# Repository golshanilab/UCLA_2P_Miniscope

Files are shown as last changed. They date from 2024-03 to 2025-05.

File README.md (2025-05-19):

# UCLA 2P Miniscope 
UCLA miniature multiphoton microscope resources and design files.

The UCLA miniscope project is an open-source inititive to design open-source miniature microscopes for neuroscience. Here, we present a multiphoton miniature microscope developed at UCLA which is able to record from fine structures like dendrites, or several hundred microns into tissue.<br>
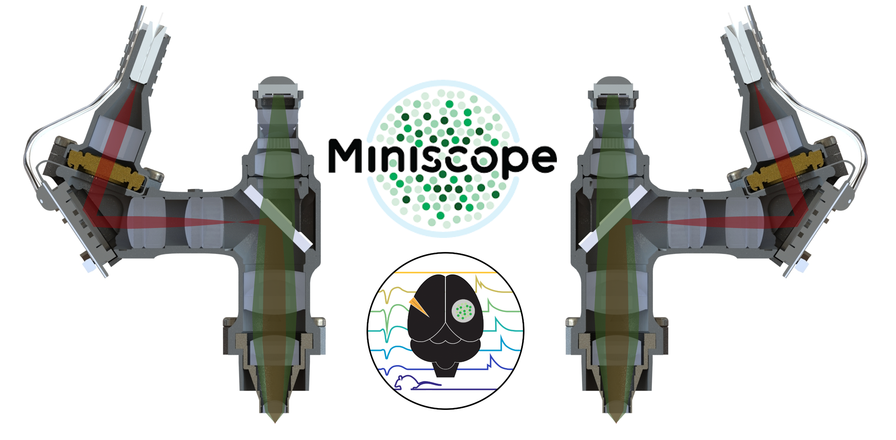
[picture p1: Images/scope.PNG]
Scope
 <br>

In this Git repository, we openly share all of the design files for this microscope with the community, these include: <br>
  - Mechanical Design Files (in .STEP format)
  - Optical Design Files (ZEMAX .ZARs)
  - Electronic PCB Designs (GERBER)
  - Control Software (Matlab and Waveforms)

<br>
As well as additional information to support users in setting up these devices, such as:

  - Suite2P analysis .ops to aid in analysis
  - A pre-trained DeepLabCut Network
  - ScanImage Machine Data Files and Configuration files
<br>

For additional information, please take a look at our bioRxiv paper [here](https://www.biorxiv.org/content/10.1101/2024.03.29.586663v1)
<br>
We also provide the following resources regarding data avialability and processing:
For a folder full of Demo resources, please visit the [Demo](https://ucla.box.com/s/3wto9k1oq8evrciismuwrfbsespp461s) UCLA Box Repository.
  - System Requirements: <br>
To analyze the data we generate, four softwares are used, [FIJI/Imagej](https://imagej.net/software/fiji/) (v.1.54f), [Suite2P](https://github.com/MouseLand/suite2p) (v.0.9.2), [DeepLabCut](https://github.com/DeepLabCut/DeepLabCut) (v.2.3.8), [MATLAB](https://www.mathworks.com/products/matlab.html) (v.2022b). Any relatively modern windows or apple computer should be capable of running all of these softwares without technical limitations, although a CUDA-compatible GPU is very useful for DeepLabCut. For this work, we tested the analysis pipeline with x64 Windows 10 Pro, v.22H2. The analysis can be completed using standard hardware, we used a Windows Book 2 from 2018 with an Intel Core i7-8650U CPU and 16BG of RAM. 

  - Software Installation Guide: <br>
Processing the data relies on well-documented software packages as well as two custom softwares. The first is a FIJI/ImageJ macro titled "Preprocess.imj" which can be installed from FIJI/ImageJ by selecting from the main toolbar "Plugins" > "Macros" > "Install" and navigating to the "Preprocess.imj" file. If you are a heavy user that anticipates routinely analyzing data, the contents of "Preprocess.imj" can be copied from the Edit Macros menu and added to the end of the "Startup Macros" file so it is installed when FIJI/ImageJ is initialized. To do so, select "Plugins" > "Macros" > "Edit" and navigate to Fiji.app\macros\StartupMacros.fiji.ijm and add the contents of "Preprocess.imj" to the end of the file. Save the file and restart Fiji/Imagej. This way the macro is installed and able to be run from the "Plugins" > "Macros" menu without installing each time.

Please reference the Suite2P, DeepLabCut, and MATLAB installation guides for assistance getting these softwares operational. The MATLAB file "SpatialFiring.m" can be run from any suitable MATLAB directory so long as "Fall.mat" and "Behavior_ExampleDLC_resnet50_2P_Miniscope_2Dec5shuffle1_100000_filtered.csv" are also present in that same directory, should you want to understand the method used in order to check the spatial firing properties of neurons within the UCLA 2P Miniscope FOV.

The total install time for the custom code is only a few minutes, installing the other standalone software can be installed within a few hours. 
    
  - Demo: <br>
Once the data is collected, there are several steps to complete the analysis. We will explain the general implementation of these steps through an example which involves processing the calcium imaging data, behavioral data, and integrating the results with a MATLAB script. 
1. First, we will condiser the calcium data. Load the .tif file "Example_Data.tif" located in the [Demo](https://ucla.box.com/s/3wto9k1oq8evrciismuwrfbsespp461s) box link, that was generated by ScanImage, into FIJI/ImageJ and preprocess using the provided "Preprocess.imj" macro. Users can also deinterleave image channels at this time. In the case of the demo, please select deinterleave on "Example_Data.tif" since it contains information from both SiPM channels. Once processed, save dynamic iamge stack (should be called "Example_Data-1.tif #1") as a .tiff ("File" > "Save As" > "Tiff"). Next initilize Suite2P v.0.9.2 and navigate to "File" > "Run Suite2P". Next, load the predefined ops.npy file in the "Load ops file" window and define the data_path field to where you saved the .tif file. Small modifications to parameters might be needed for your specific use case, these are general and what worked well in our hands. Next click "RUN SUITE2P" and wait until all data is processed. Within the "save_path" directory, there will be a "Fall.mat" file contained in the "suite2p" > "plane0" folder which we will then process. Screenshots of the expected output are included within the Demo folder as "Demo_S2P_Output.PNG". 
2. Next, analyze the time-synchronized example behavior video "Behavior_Demo.avi" with DeepLabCut. For this example, the calcium and behavior videos are not aligned. If this is your first time, please review the excellent documentation found [here](https://deeplabcut.github.io/DeepLabCut/docs/installation.html) to label data and build a trained model. We have included a pre-trained network that we used for image classification of the location of the miniscope headpiece, but it may be necessary to build your own model depending on your specific experimental conditions. Output files "Behavior_ExampleDLC_resnet50_2P_Miniscope_2Dec5shuffle1_100000_filtered.csv" are provided along with an annotated video describing the DeepLabCut outputs. Once complete, navigate to the "video" directory of your DLC model and select the DLC output .csv file and place in the same directory as the "SpatialFiring.m" file. We provide this processed .csv file as "Behavior_ExampleDLC_resnet50_2P_Miniscope_2Dec5shuffle1_100000_filtered.csv" within the "Demo" > "Expected Outputs" > "DeepLabCut" folder. 
3. Now that the calcium imaging and behavior data are analyzed, we can put the two together and assess the firing properties of individual neurons as a function of location in the behavioral chamber and time. For this purpose use the "SpatialFiring.m" file included in this repository and to the same directory add the "Fall.mat" and the output of the DLC process, which in the uploaded example is called "Behavior_ExampleDLC_resnet50_2P_Miniscope_2Dec5shuffle1_100000_filtered.csv." This will compute the spatial firing properties of the neural traces from "Fall.m" based on the spatial coordinates found in the "Behavior_ExampleDLC_resnet50_2P_Miniscope_2Dec5shuffle1_100000_filtered.csv" file.

We also provide in the [Demo](https://ucla.box.com/s/3wto9k1oq8evrciismuwrfbsespp461s) folder, the expected output from the analysis described above. The preprocessing step in FIJI/Imagej took approximately 2 minutes to complete, Suite2P analysis took 7 minutes with all of the registration steps and ROI extraction for the 1000 frames of the first channel from the "Example_Data.tif" demo file. DeepLabCut took approximately 4 minutes to process the "Example_Behavior.mp4" video on a computer fitted with an NVIDIA GeForce 1060 GPU. 
    
  - Instructions For Use: <br>
The demo section of this GitHub repo is intended to explain how to use the software through a concrete provided example. Any user can replace the example microscope imaging data and behavioral video, to reproduce the same sorts of outputs that are described in the manuscript.  
<br>
  - Small-Amplitude Striping Artifact: <br>
Through our testing, we have noticed a reproducible, small-amplitude striping artifact that can be present in very low-light imaging conditions. We believe this to be due to capacitive coupling between the high voltage driving waveform (on the x-axis of the MEMS scanner specifically) and the small-amplitude SiPM signal currents that pass alongside the high voltage drive signal prior to transimpedance amplification. We have included a custom FFT signal filter and built a Fiji macro around it, to selectively remove this high frequency artifact from single frames or image stacks. These resources have been uploaded under Guides, Image Filtering as FFT_Filter.tif” and “Preprocess_Filter.ijm” respectively. Additionally, two images are included to demonstrate an example of the artifact in question and the results of the filter. The images included are mean intensity projections from a time course of 2746 frames prior to motion correction, to highlight the artifact. Small amounts of residual striping still exist after filtering, but the overall impact is greatly diminished. Of note, in parallel we have developed new wiring strategies that increase coaxial shielding to eliminate the striping altogether. Updated wiring diagrams will be included on this repository soon to eliminate the artifact entirely. 
<br>
Here are some fancy images that show off what the microscope is capable of!
<br>
This is a densely-labled CA1 expressing GCaMP7f.

CA1 <br>
<br>
This is RSC expressing GCaMP6f and an mCherry c-Fos reporter.
<br>
RSC
<br>
This is an exploded view of the microscope, including all of the mechanical and optical components. <br>
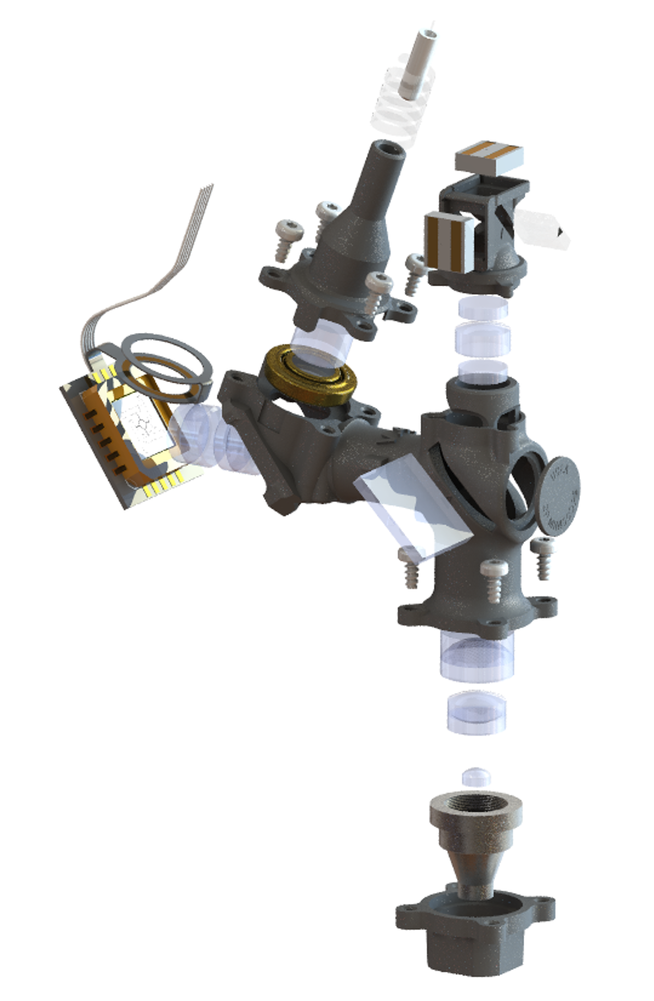
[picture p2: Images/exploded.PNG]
This is an exploded view of the microscope, including all of the mechanical and optical components.
<br>

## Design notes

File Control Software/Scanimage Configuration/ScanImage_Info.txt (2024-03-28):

These files are what we are currently using to control the UCLA 2P Miniscope from within ScanImage

You may need to modify the machine data file to support your specific application

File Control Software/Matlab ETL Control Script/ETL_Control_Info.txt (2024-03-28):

If you’re planning on controlling the tunable lens from within MATLAB, run the “ETL_Control” script alongside the compatible NI control electronics. 

This GUI will enable online control of focal position during experiments. 

The I2C Hardware support library is also required and can be found here:
https://www.mathworks.com/hardware-support/i2c-interface.html

In the future, i2c control will be integrated into a custom python GUI.

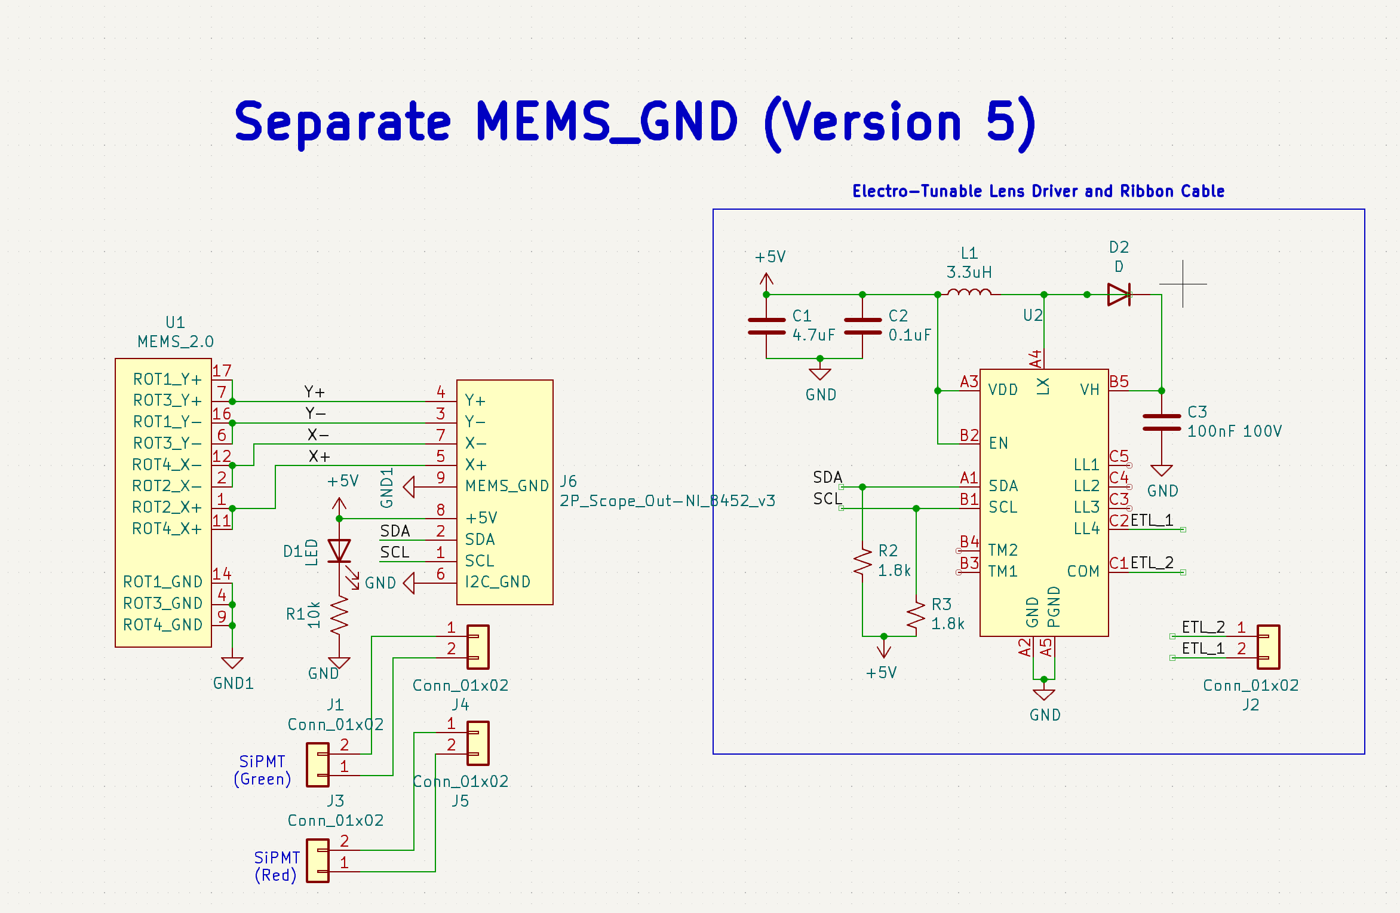
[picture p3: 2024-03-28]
Electronic Designs/UCLA 2P Miniscope FLEX-PCB/Schematic.PNG

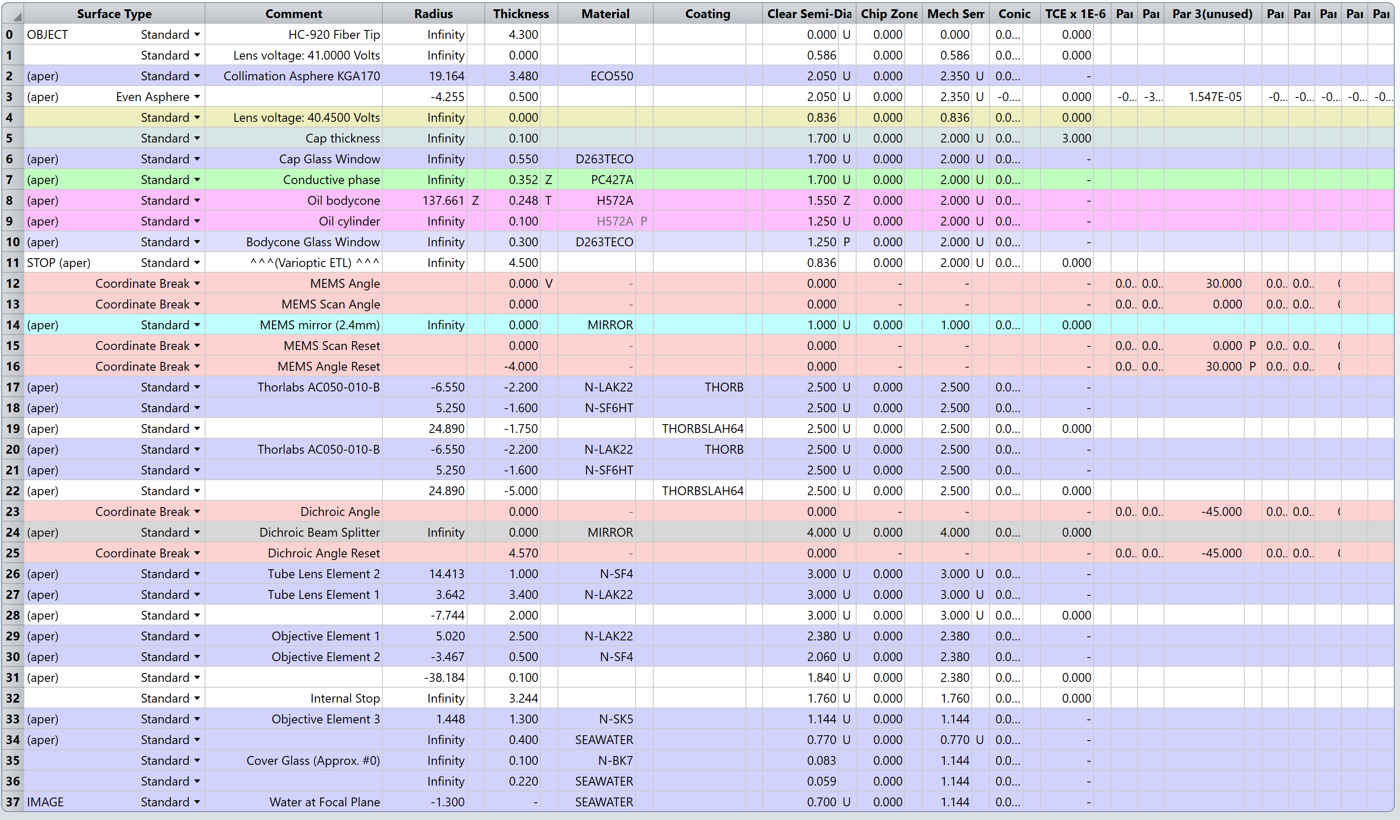
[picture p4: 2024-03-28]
ZEMAX Optical Designs/Excitation_Optical_System.PNG

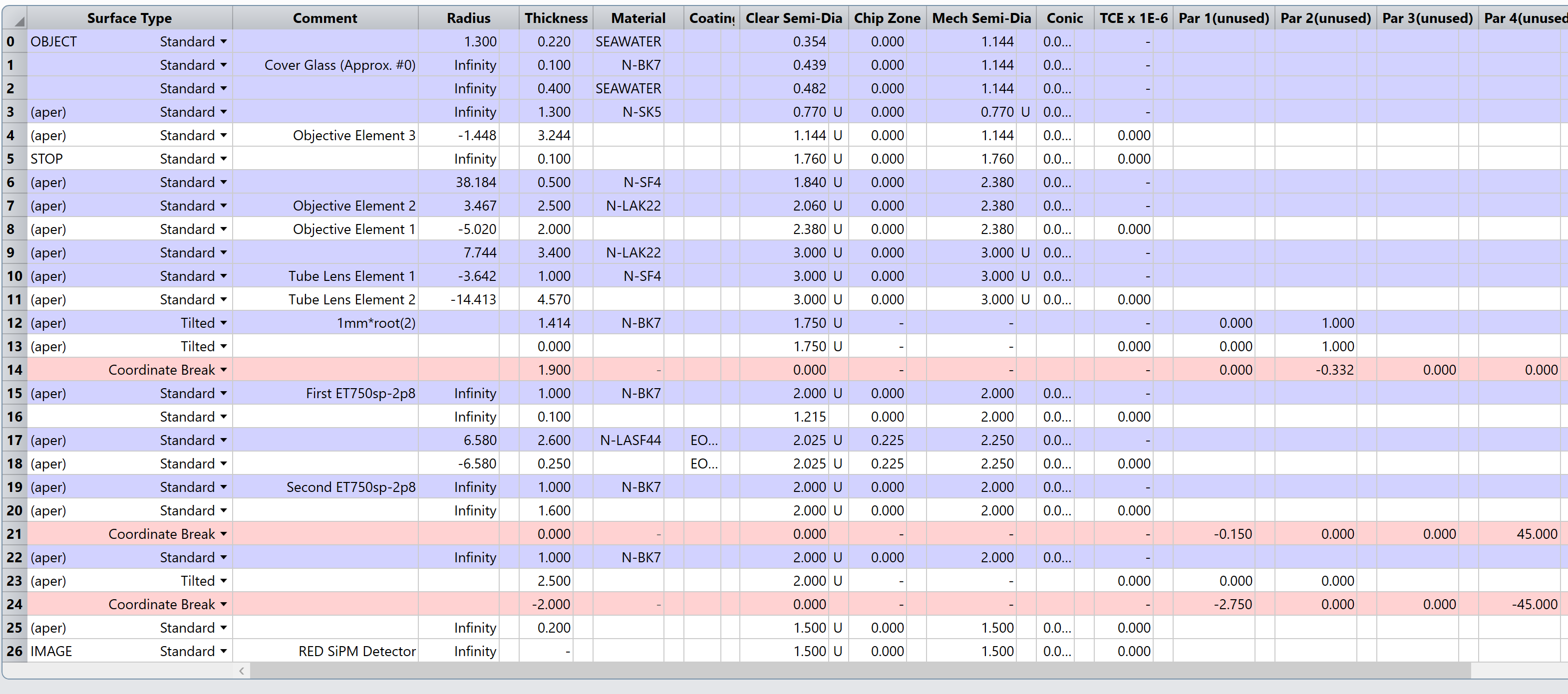
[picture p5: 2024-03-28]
ZEMAX Optical Designs/Emission_Optical_System_Red.PNG

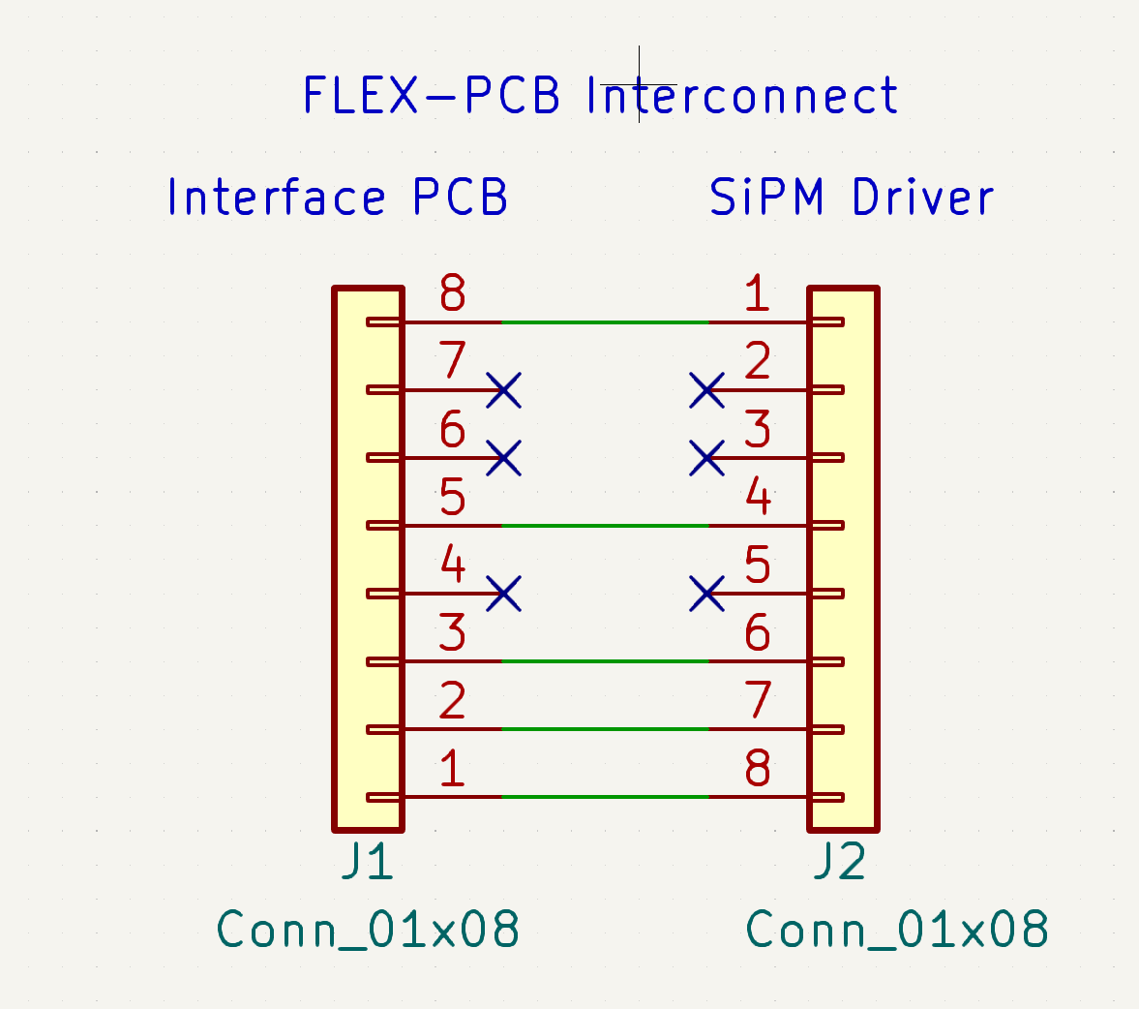
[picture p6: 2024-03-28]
Electronic Designs/UCLA 2P Miniscope Interface FLEX-PCB/Schematic.PNG

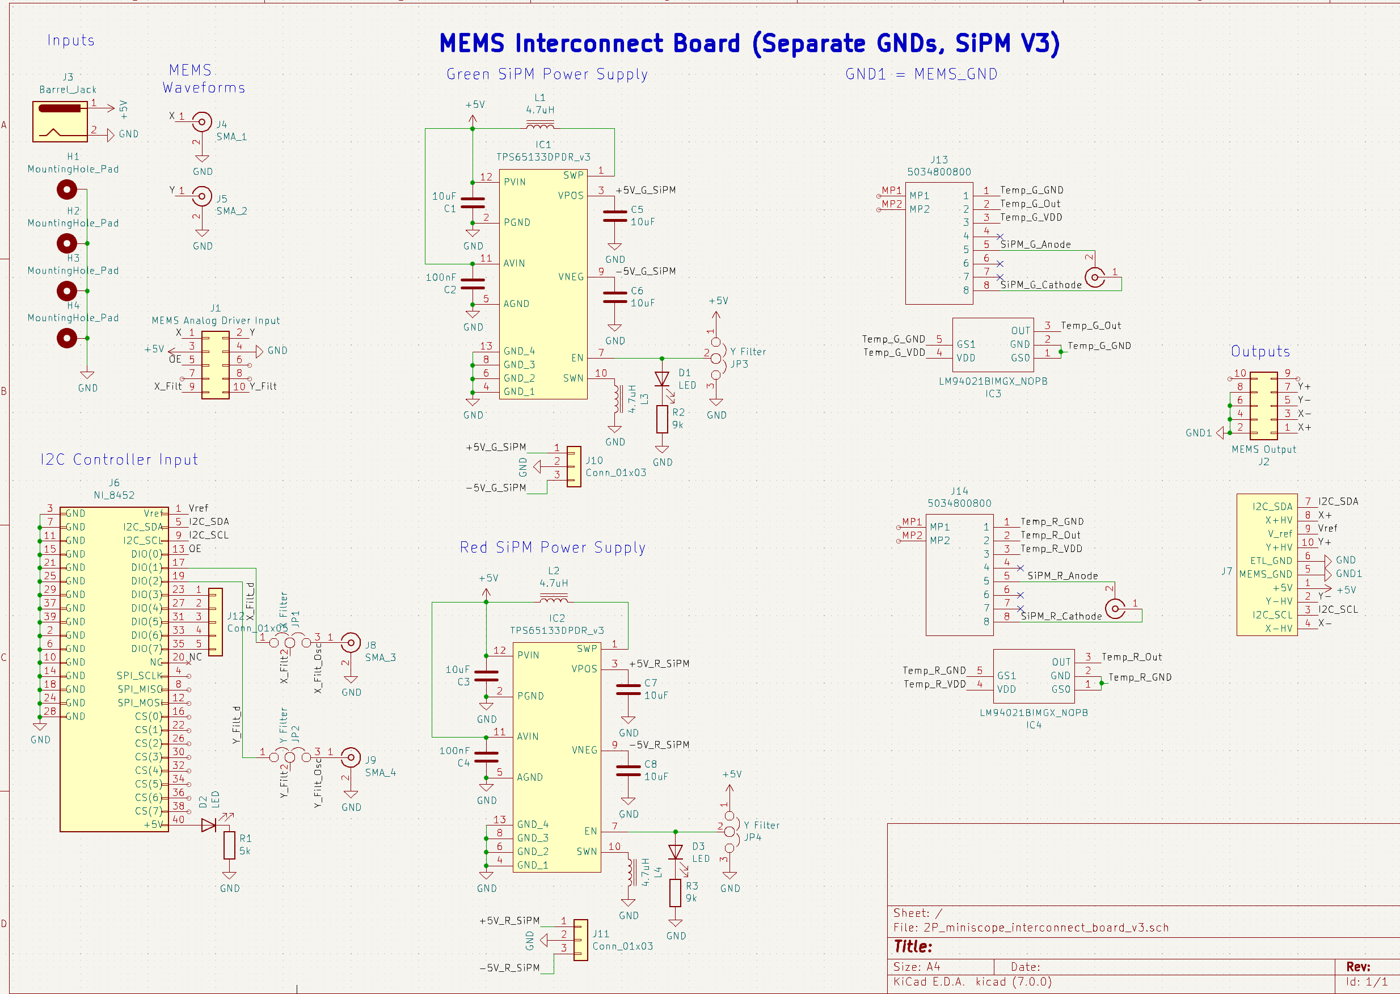
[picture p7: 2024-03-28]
Electronic Designs/UCLA 2P Miniscope Interface PCB/Schematic.PNG

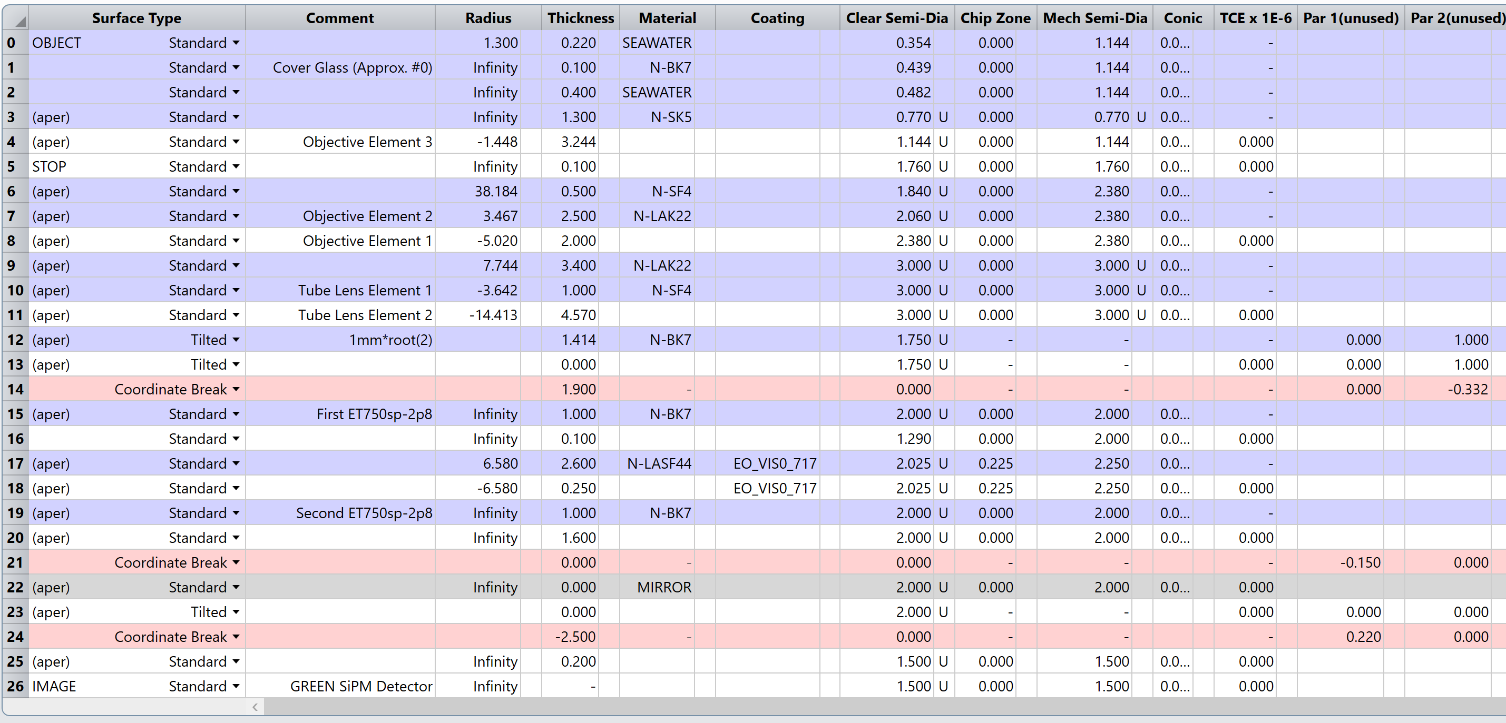
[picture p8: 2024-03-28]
ZEMAX Optical Designs/Emission_Optical_System_Green.PNG

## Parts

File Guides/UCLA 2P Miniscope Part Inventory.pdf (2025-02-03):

UCLA 2P Miniscope Assembly Guide Component Inventory and Validations The first step in assembly is to validate all components are sourced and ready to be used. For the headpiece, it’s straightforward to think about breaking the parts down into their respective subassemblies and ensure that all parts are assembled. Please find links to each component either within the GitHub

repository or respective manufacturer. Some components, like the electronic PCBs,

the custom lenses made by Optics Technology, and diced filters, are custom made or modified and need to be either constructed yourself or with the help of manufacturers. We are hoping to put together batch orders for components such that users can receive all needed parts for fabrication in a single shipment. For more information please contact pgolshani@mednet.ucla.edu

## These components are required for the Main Housing Assembly:

Component | Part Number | Manufacturer | Unit | Price | Subtotal | Link
Main Housing | Main_Housing.STL | Custom | 1 | $1.00 | $1.00 | Main Housing (https://github.com/golshanilab/UCLA_2P_Miniscope/blob/main/Mechanical%20Designs/STLs%20to%203D%20Print/Main_Housing.STL)
Lens Cover | Lens_Cover.STL | Custom | 1 | $1.00 | $1.00 | Lens Cover (https://github.com/golshanilab/UCLA_2P_Miniscope/blob/main/Mechanical%20Designs/STLs%20to%203D%20Print/Lens_Cover.STL)
Flex-PCB | FLEX-PCB | Custom | 1 | $600.00 | $600.00 | Flex-PCB (https://github.com/golshanilab/UCLA_2P_Miniscope/tree/main/Electronic%20Designs/UCLA%202P%20Miniscope%20FLEX-PCB)
Scan Lens | AC050-010-B | ThorLabs | 2 | $51.38 | $102.76 | Scan Lens (https://www.thorlabs.com/thorproduct.cfm?partnumber=AC050-010-B)
Tube Lens* | OT-1 (Custom) | Optics Technology | 1 | $1,100.0 0 | $1,100.0 0 | Tube Lens (https://github.com/golshanilab/UCLA_2P_Miniscope/blob/main/ZEMAX%20Optical%20Designs/Excitation_Path_Full_System.zar)
2P Dichroic (Diced) | ZT775sp-2p, 8x8.5x1mm | Chroma | 1 | $540.00 | $540.00 | 2P Dichroic (https://www.chroma.com/products/parts/zt775sp-2p-multiphoton-shortpass-laser-dichroic)
Torx Screws | 96817A704 | McMaster-Carr | 4 | $0.63 | $2.53 | Torx Screws (https://www.mcmaster.com/96817A704/)
Optical Glue | NOA68 | Norland | 1 | $40.70 | $40.70 | Optical Glue (https://www.thorlabs.com/thorproduct.cfm?partnumber=NOA68)
| | | | | $2,387.9 9

* Tube lens is custom fabricated, please contact pgolshani@mednet.ucla.edu for more information

## The following components are required for the Detector Assembly:

Component | Part Number | Manufacturer | Unit | Price | Subtota l | Link
Detector Housing | Detector_Housing.STL | Custom | 1 | $1.00 | $1.00 | Detector Housing (https://github.com/golshanilab/UCLA_2P_Miniscope/blob/main/Mechanical%20Designs/STLs%20to%203D%20Print/Detector_Housing.STL)
Emission Filter Support | Emission_Filter_Support.ST L | Custom | 1 | $1.00 | $1.00 | Emission Support (https://github.com/golshanilab/UCLA_2P_Miniscope/blob/main/Mechanical%20Designs/STLs%20to%203D%20Print/Emission_Filter_Support.STL)
Collection Lens | 47-895 | Edmund Optics | 1 | $62.50 | $62.50 | Collection Lens (https://www.edmundoptics.com/p/45mm-dia-x-45mm-fl-vis-0deg-coated-double-convex-lens/8081/)
Emission Filter (Cut)* | ET750sp, 4mm OD x1mm | Chroma | 2 | $150.00 | $300.00 | Emission Filter (https://www.chroma.com/products/parts/et750sp-2p8-multiphoton-shortpass-emission-filter)
1P Dichroic (Diced)** | T550lpxr, 4x4x1mm | Chroma | 1 | $112.50 | $112.50 | 1P Dichroic (https://www.chroma.com/products/parts/t550lpxr)
SiPM Detector | S13360-3075PE | Hamamatsu | 2 | $52.88 | $105.76 | SiPM Detector (https://www.hamamatsu.com/us/en/product/optical-sensors/mppc/mppc_mppc-array/S13360-3075PE.html)
| | | | | $582.76
* The emission filter used is a modified form of the ET750sp-2p8 (linked) to reduce the thickness

** The cost per filter was reduced in our order due to multiple 4mm filters being produced from one standard filter after dicing

## The following components are required for the Collimator Assembly:

Component | Part Number | Manufacturer | Unit | Price | Subtotal | Link
Collimator Housing | Collimator_Housing.STL | Custom | 1 | $1.00 | $1.00 | Collimator Housing (https://github.com/golshanilab/UCLA_2P_Miniscope/blob/main/Mechanical%20Designs/STLs%20to%203D%20Print/Collimator_Housing.STL)
Collimation Asphere | KGA170-B | Newport | 1 | $107.0 0 | $107.00 | Collimation Asphere (https://www.newport.com/p/KGA170-B)
ETL | A-25H1 | Varioptic | 1 | $135.0 0 | $135.00 | ETL (https://www.corning.com/au/en/products/advanced-optics/product-materials/corning-varioptic-lenses/variable-focus-lenses-a-series/varioptic-A-25H.html)
Torx Screws | 96817A704 | McMaster-Carr | 4 | $0.63 | $2.53 | Torx Screws (https://www.mcmaster.com/96817A704/)
| | | | | $245.53

## The following components are required for the Lower Housing Assembly:

Component | Part Number | Manufacturer | Unit | Price | Subtotal | Link
Lower Housing | Lower_Housing.STL | Custom | 1 | 1 | 1 | Lower Housing (https://github.com/golshanilab/UCLA_2P_Miniscope/blob/main/Mechanical%20Designs/STLs%20to%203D%20Print/Lower_Housing.STL)
Objective Lens* | OT-2 (Custom) | Optics Technology | 1 | 4000 | 4000 | Objective Lens (https://github.com/golshanilab/UCLA_2P_Miniscope/blob/main/ZEMAX%20Optical%20Designs/Excitation_Path_Full_System.zar)
O-Ring | | McMaster-Carr | 1 | 0.159 6 | 0.1596 | O-Ring (https://www.mcmaster.com/9262K118/)
| | | | | $4,001.1 6

* Tube lens is custom fabricated, please contact pgolshani@mednet.ucla.edu for more information

## The necessary tools for assembling the microscope are:

Component | Part Number | Manufacturer | Unit | Price | Subtotal | Link
UV-Curing System* | CS20K2 | ThorLabs | 1 | $2,634.6 6 | $2,634.66 | UV-Curing System (https://www.thorlabs.com/thorproduct.cfm?partnumber=CS20K2)
Flathead Driver | 84705260150 | Wiha | 1 | $5.17 | $5.17 | Flathead Driver (https://www.wihatools.com/products/precision-slotted-1-5-1-16-x-40mm)
Torx Screwdriver | 52995A24 | McMaster-Carr | 1 | $9.48 | $9.48 | Torx Driver (https://www.mcmaster.com/52995A24/)
Scan Lens Reamer | 8851A18 | McMaster-Carr | 1 | $24.18 | $24.18 | Scan Lens Reamer (https://www.mcmaster.com/8851A18/)
Tube Lens Reamer | 8851A21 | McMaster-Carr | 1 | $28.78 | $28.78 | Tube Lens Reamer (https://www.mcmaster.com/8851A21/)
Ferrule Reamer | 2777A128 | McMaster-Carr | 1 | $116.97 | $116.97 | Ferrule Reamer (https://www.mcmaster.com/2777A128/)
| | | | | $2,819.24
*This is the replacement for what we use in the lab (now obsolete part no. LED-200, ThorLabs)

Please note that there are also custom interface circuits that are needed to build the complete system. They are covered in another document and are not referenced in this document further since the main purpose is to describe the method for constructing the microscope headpiece itself. Additionally, you will

need an appropriate length of cleaved and sealed HC-920 optical fiber. For now,

## we will assume that the reader has appropriately launched the 2P laser to the HC-

920 optical fiber, with sufficient efficiency.

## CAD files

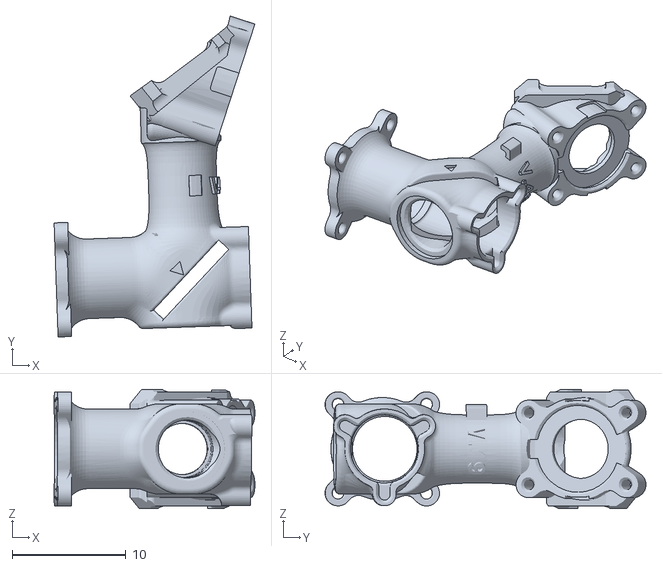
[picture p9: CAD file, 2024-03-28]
Mechanical Designs/STLs to 3D Print/Main_Housing.STL
17.6 x 28.2 x 10.5

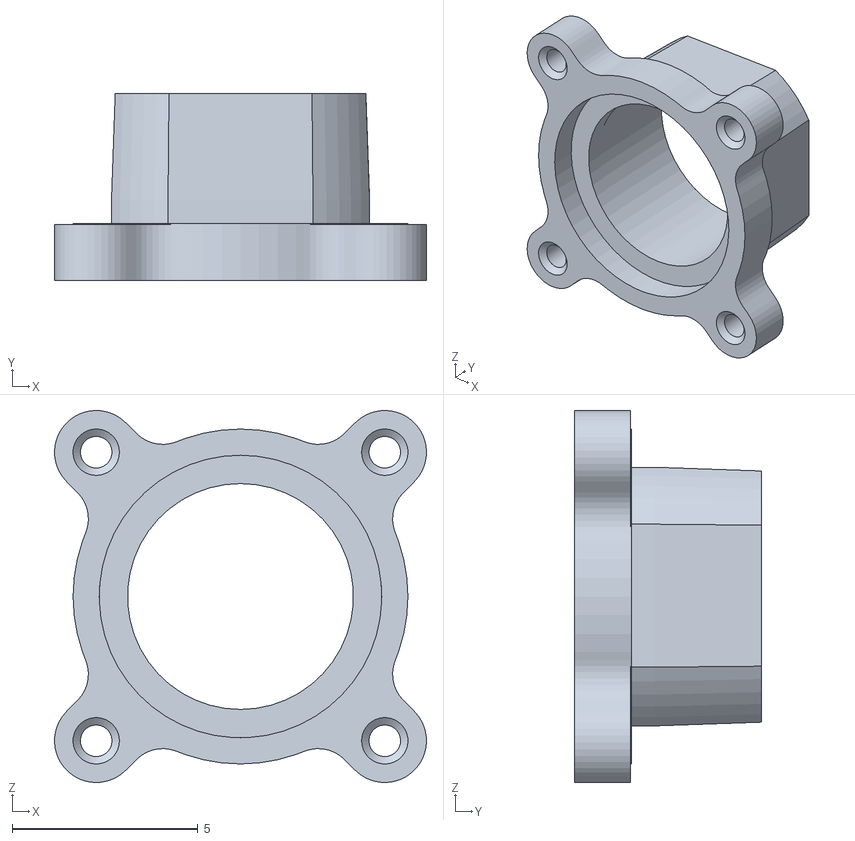
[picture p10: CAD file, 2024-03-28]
Mechanical Designs/STLs to 3D Print/Lower_Housing.STL
10.0 x 5.03 x 10.0

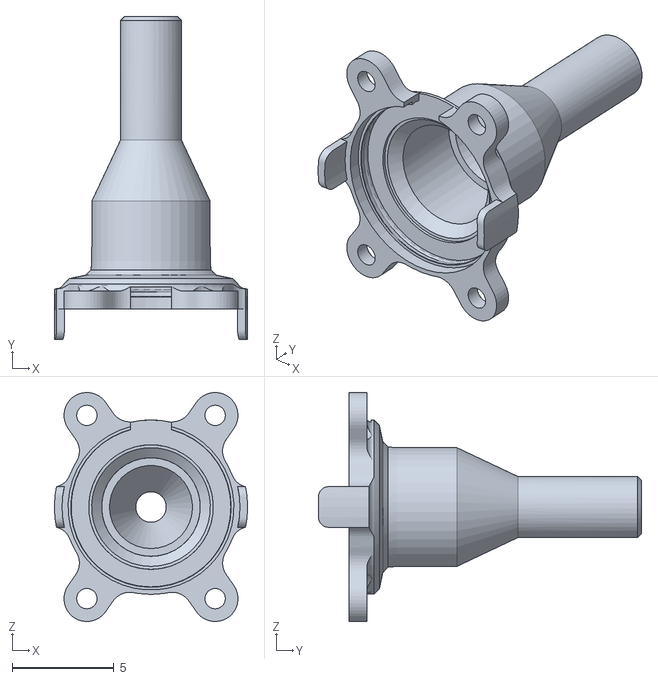
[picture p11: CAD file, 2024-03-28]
Mechanical Designs/STLs to 3D Print/Collimator_Housing.STL
9.50 x 15.9 x 11.3

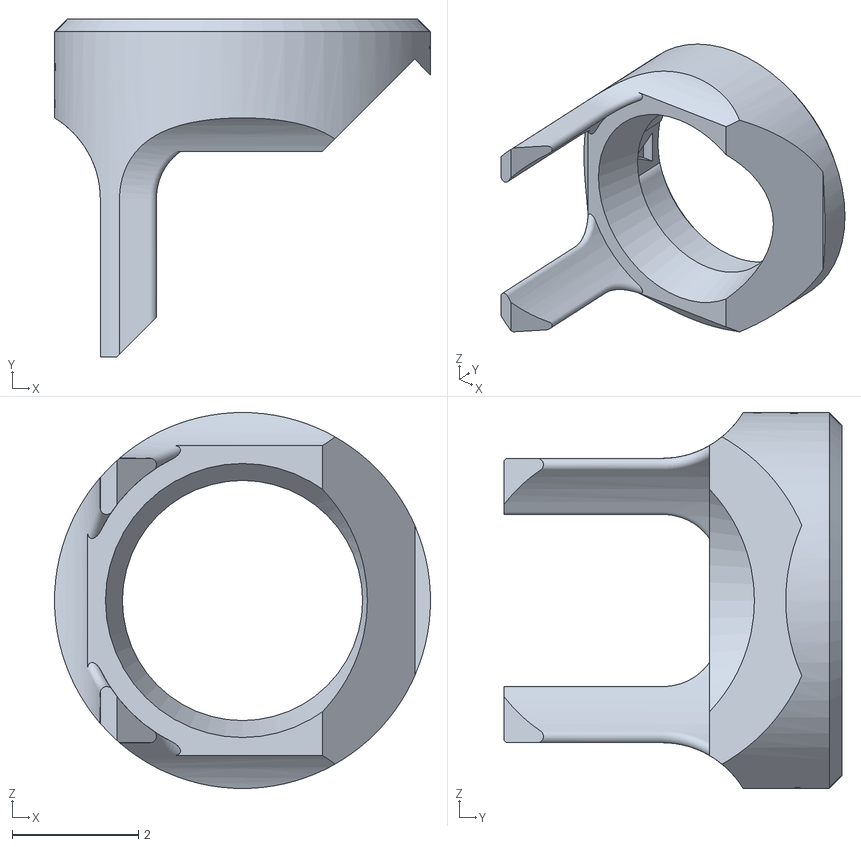
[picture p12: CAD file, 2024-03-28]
Mechanical Designs/STLs to 3D Print/Emission_Filter_Support.STL
5.95 x 5.35 x 5.95

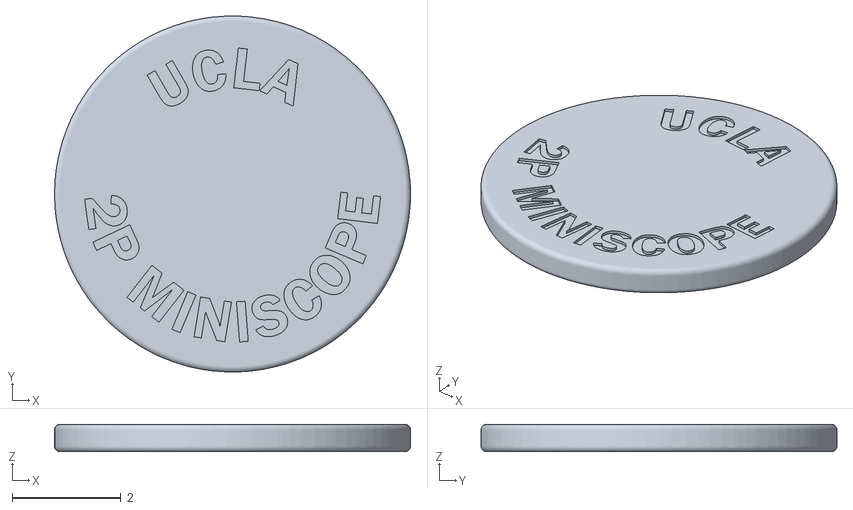
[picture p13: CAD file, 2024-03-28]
Mechanical Designs/STLs to 3D Print/Lens_Cover.STL
6.54 x 6.54 x 0.5

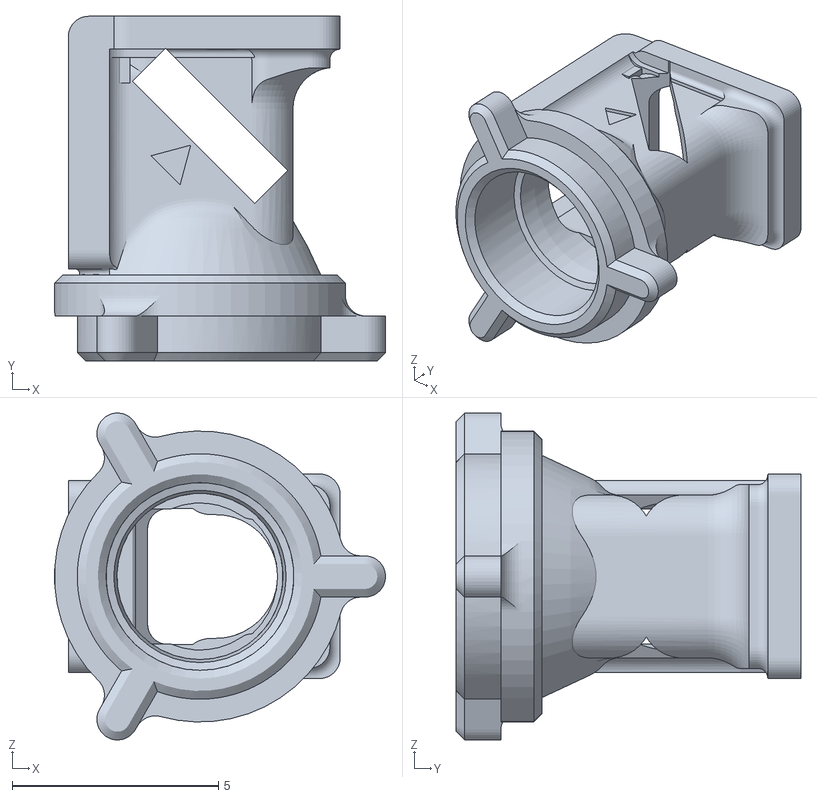
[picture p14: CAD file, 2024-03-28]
Mechanical Designs/STLs to 3D Print/Detector_Housing.STL
8.03 x 8.36 x 7.93

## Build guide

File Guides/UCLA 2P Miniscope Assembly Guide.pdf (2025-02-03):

## UCLA 2P Miniscope Assembly Guide

You’ve decided to assemble a UCLA 2P Miniscope! That’s wonderful, and it is our sincere goal to help walk you through that process to make it as intuitive and straightforward as possible. This document will be updated over time following user feedback and serves as a constantly improving guide to constructing the microscope headpiece. We are still in early stages here, and we are hoping to make this open-source project as useful as possible. Please reach out to bmadruga@physics.ucla.edu and pgolshani@mednet.ucla.edu with any questions.

Table of Contents:
Assembly Tools
1. Collimator Assembly
2. Detector Assembly
3. Lower Housing Assembly
4. Main Housing Assembly

The necessary tools for assembling the microscope are:

Component | Part Number | Manufacturer | Unit | Price | Subtotal | Link
UV-Curing Gun | LED-200 | Electro-Lite | 1 | $1,932 | $1,932 | UV-Curing Gun (http://www.electro-lite.com/PDFs/LED-200.pdf)
Flathead Driver | 84705260150 | Wiha | 1 | $5.17 | $5.17 | Flathead Driver (https://www.wihatools.com/products/precision-slotted-1-5-1-16-x-40mm)
Torx Screwdriver | 52995A24 | McMaster-Carr | 1 | $9.48 | $9.48 | Torx Driver (https://www.mcmaster.com/52995A24/)
Scan Lens Reamer | 8851A18 | McMaster-Carr | 1 | $24.18 | $24.18 | Scan Lens Reamer (https://www.mcmaster.com/8851A18/)
Tube Lens Reamer | 8851A21 | McMaster-Carr | 1 | $28.78 | $28.78 | Tube Lens Reamer (https://www.mcmaster.com/8851A21/)
Collection Lens Reamer | 8851A17 | McMaster-Carr | 1 | $23.63 | $23.63 | Collection Lens Reamer (https://www.mcmaster.com/8851A17/)
Ferrule Reamer | 8803A156 | McMaster-Carr | 1 | $21.61 | $21.61 | Ferrule Reamer (https://www.mcmaster.com/8803A156/)
NIR Viewing Card | VRC4 | ThorLabs | 1 | $94.05 | $94.05 | NIR Viewing Card (https://www.thorlabs.com/thorproduct.cfm?partnumber=VRC4)
| | | | | $2,138.90
These tools are what we use in the lab to assemble the microscope headpieces. There are certainly other alternatives or other approaches to building these microscopes. We are just providing what worked well for us.

Now that we confirmed that all of the necessary tools are present, we will break the microscope down into 4 subassemblies. First, we will build the simple subassemblies, then we will build the main housing and combine that main housing with the other subassemblies.

### 1. Collimator Assembly

The following components are required for the Collimator Assembly. Please verify that all components are sourced before beginning.

Component | Part Number | Manufacturer | Unit | Price | Subtotal | Link
Collimator Housing | Collimator_Housing.STL | Custom | 1 | $1.00 | $1.00 | Collimator Housing (https://github.com/golshanilab/UCLA_2P_Miniscope/blob/main/Mechanical%20Designs/STLs%20to%203D%20Print/Collimator_Housing.STL)
Collimation Asphere | KGA170-B | Newport | 1 | $107.00 | $107.00 | Collimation Asphere (https://www.newport.com/p/KGA170-B)
ETL | A-25H1 | Varioptic | 1 | $135.00 | $135.00 | ETL (https://www.corning.com/au/en/products/advanced-optics/product-materials/corning-varioptic-lenses/variable-focus-lenses-a-series/varioptic-A-25H.html)
Torx Screws | 96817A704 | McMaster-Carr | 4 | $0.63 | $2.53 | Torx Screws (https://www.mcmaster.com/96817A704/)
| | | | | $245.53
Building the Collimator consists of 10 steps in total.
1. Collect Collimator Housing and 1.8mm Fiber Ferrule Reamer.
2. Ream the fiber input to 1.8mm in order to tightly support the optical fiber ferrule.
3. Check the fit of the ferrule in the housing using the input hollow core optical fiber. The goal is to ensure a snug fit with enough play to allow for axial positioning of the ferrule within the collimator housing. We will eventually ensure that the distance is optimal by checking the collimation of the light following the asphere.
4. Partially install the torx screws, as this makes joining the collimator and main housing assemblies far easier down the road.

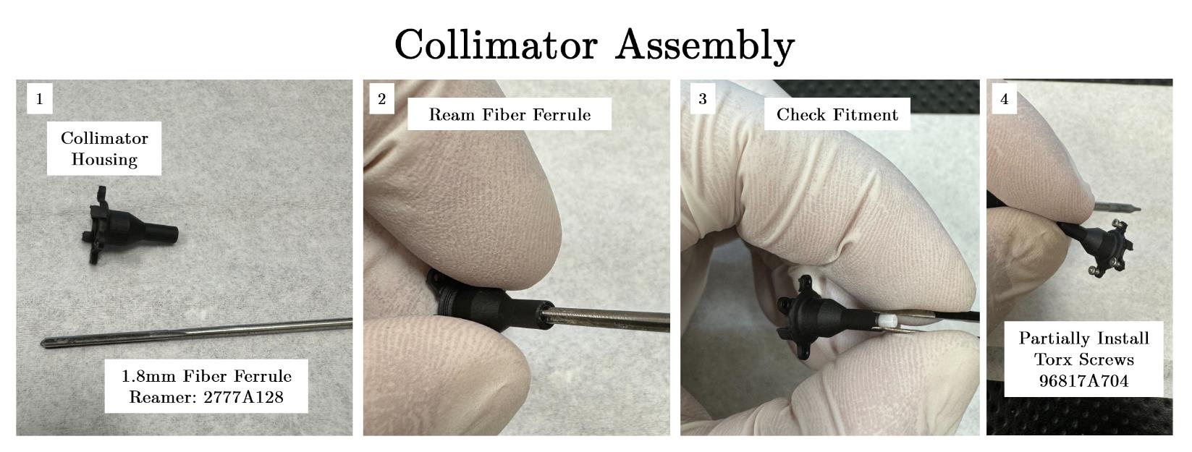
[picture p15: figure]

5. Prepare the collimation asphere and ensure that the directionality is correct based on the optical model and supplied figure. The more flat surface is oriented closest to the fiber input.
6. Install asphere until pressed into the fixed stop in collimator housing.
7. Add a small amount of NOA68 to one corner of the lens (minimize the amount of clear aperture obscured) and cure using a UV lamp.

8. Install fiber ferrule that is aligned to the 2P laser and emit a small amount of laser power from the 2P laser (< 20mW).
9. Check the collimation state of the laser after the asphere and modulate the axial position of the fiber ferrule within the collimator to optimize. The diameter of the laser beam should remain constant from the front surface of the asphere, to ideally, infinity. In our hands, we ensure minimal divergence over approximately 2 meters and it seems to produce expected results. To visualize the laser beam, we suggest using the VRC4 NIR viewing card from ThorLabs.
10. Once divergence is minimized and the laser is well collimated, add a small amount of NOA68 to the interface of the collimator housing and the fiber ferrule to keep the fiber in the correct position.

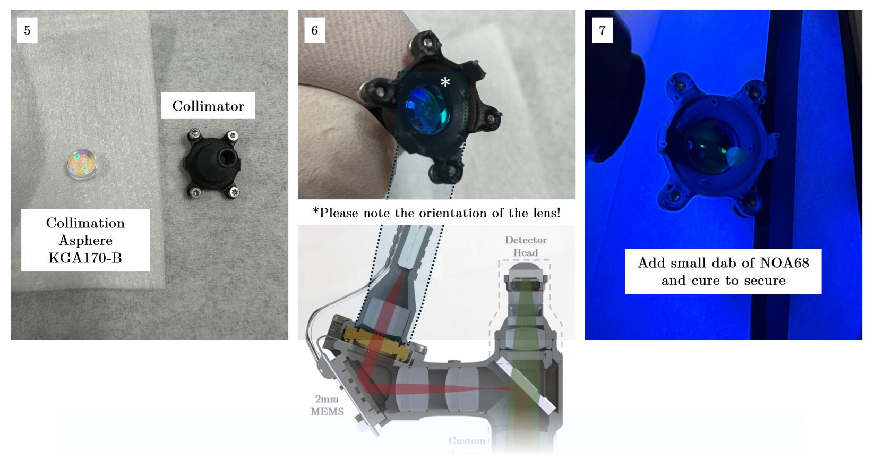
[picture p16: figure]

### 2. Lower Housing Assembly

The following components are required for the Lower Housing Assembly. Please verify that all components are sourced before beginning.

Component | Part Number | Manufacturer | Unit | Price | Subtotal | Link
Lower Housing | Lower_Housing.STL | Custom | 1 | 1 | 1 | Lower Housing (https://github.com/golshanilab/UCLA_2P_Miniscope/blob/main/Mechanical%20Designs/STLs%20to%203D%20Print/Lower_Housing.STL)
Objective Lens* | OT-2 (Custom) | Optics Technology | 1 | 4000 | 4000 | Objective Lens (https://github.com/golshanilab/UCLA_2P_Miniscope/blob/main/ZEMAX%20Optical%20Designs/Excitation_Path_Full_System.zar)
O-Ring | | McMaster-Carr | 1 | 0.1596 | 0.1596 | O-Ring (https://www.mcmaster.com/9262K118/)
| | | | | $4,001.16
* Tube lens is custom fabricated, please contact pgolshani@mednet.ucla.edu for more information

The lower housing can be built in only 3 steps.

1. Collect all necessary components
2. Install O-Ring into the lower housing
3. Press the objective lens into the lower housing

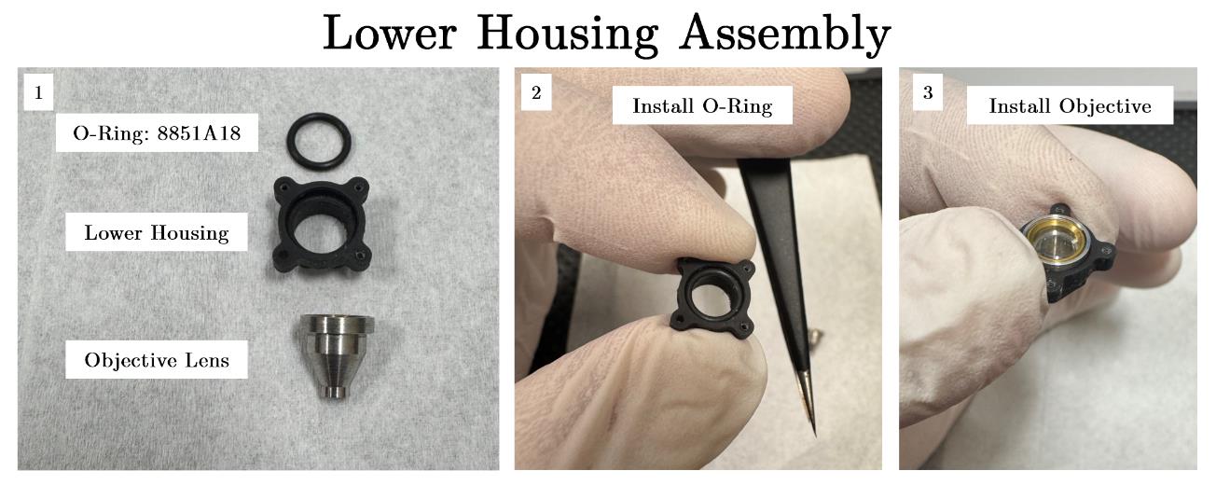
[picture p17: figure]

### 3. Detector Assembly:

The following components are required for the Detector Assembly. Please verify that all components are sourced before beginning.

Component | Part Number | Manufacturer | Unit | Price | Subtotal | Link
Detector Housing | Detector_Housing.STL | Custom | 1 | $1.00 | $1.00 | Detector Housing (https://github.com/golshanilab/UCLA_2P_Miniscope/blob/main/Mechanical%20Designs/STLs%20to%203D%20Print/Detector_Housing.STL)
Emission Filter Support | Emission_Filter_Support.ST L | Custom | 1 | $1.00 | $1.00 | Emission Support (https://github.com/golshanilab/UCLA_2P_Miniscope/blob/main/Mechanical%20Designs/STLs%20to%203D%20Print/Emission_Filter_Support.STL)
Collection Lens | 47-895 | Edmund Optics | 1 | $62.50 | $62.50 | Collection Lens (https://www.edmundoptics.com/p/45mm-dia-x-45mm-fl-vis-0deg-coated-double-convex-lens/8081/)
Emission Filter (Cut)* | ET750sp, 4mm OD x1mm | Chroma | 2 | $150.00 | $300.00 | Emission Filter (https://www.chroma.com/products/parts/et750sp-2p8-multiphoton-shortpass-emission-filter)
1P Dichroic (Diced)** | T550lpxr, 4x4x1mm | Chroma | 1 | $112.50 | $112.50 | 1P Dichroic (https://www.chroma.com/products/parts/t550lpxr)
SiPM Detector | S13360-3075PE | Hamamatsu | 2 | $52.88 | $105.76 | SiPM Detector (https://www.hamamatsu.com/us/en/product/optical-sensors/mppc/mppc_mppc-array/S13360-3075PE.html)
| | | | | $582.76
* The emission filter used is a modified form of the ET750sp-2p8 (linked) to reduce the thickness

** The cost per filter was reduced in our order due to multiple 4mm filters being produced from one standard filter after dicing

The Detector Assembly is constructed in 9 steps. The process involves putting together two components, the Emission Filter Support and the main Detector Housing.

1. Collect all necessary components listed above.
2. Install emission filter 1 into the emission filter support making sure of filter orientation.

3. Ream the detector housing using the collection lens reamer to ensure a secure fit. Take care not to ream excessively far as it will disrupt the mounting surface for the emission filer 2.

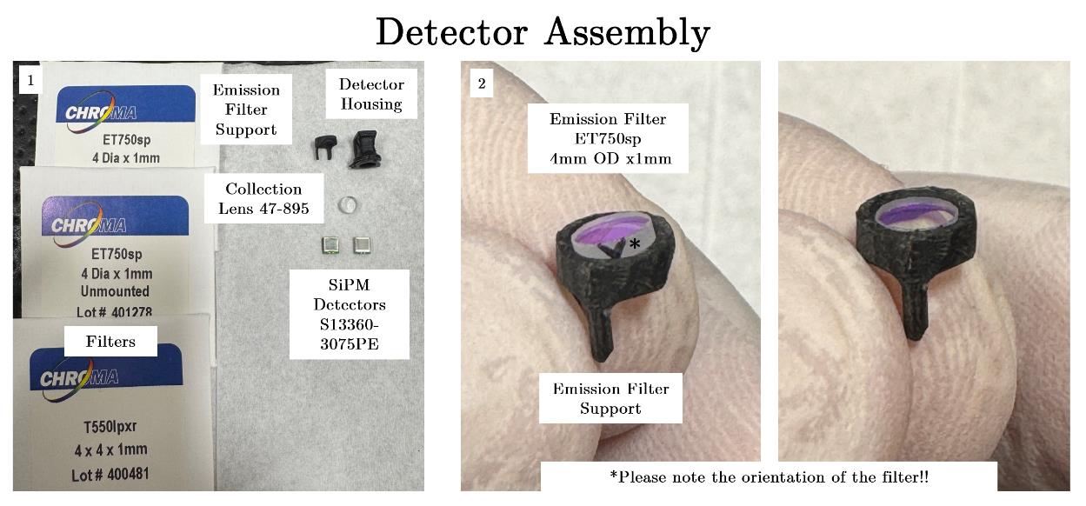
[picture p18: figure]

4. Install emission filter 2 making sure to orient the filter with the arrow oriented correctly.
5. Install collection lens (orientation does not matter in this case).
6. Ensure that the lens is fully seated in place, the lens should be nearly flush with the front of the detection housing.

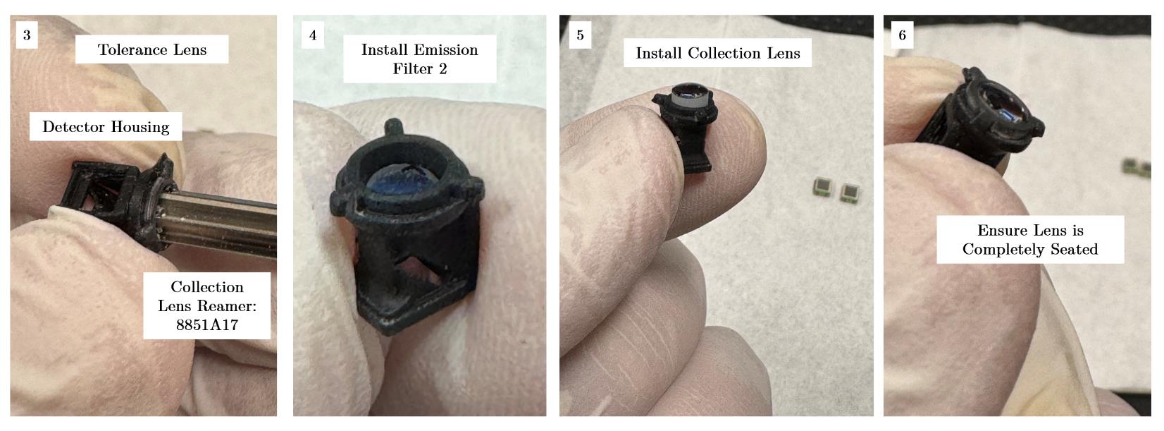
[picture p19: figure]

7. Install the 1P dichroic mirror that splits the fluorescent signal between the two SiPM detectors. Make sure the arrowhead is pointing at the arrowhead printed into the detector housing. Make sure it’s fully installed and supported on both sides of the housing.

8. Install the first SiPM (red). The image shows the correct orientation of the SiPM, simply imagine rotating along the longer axis, like turning the page of a book.
9. Install the second SiPM (green) in the same way as described in
step 8.
10. Fix the SiPMs and dichroic will very small amounts of NOA68.

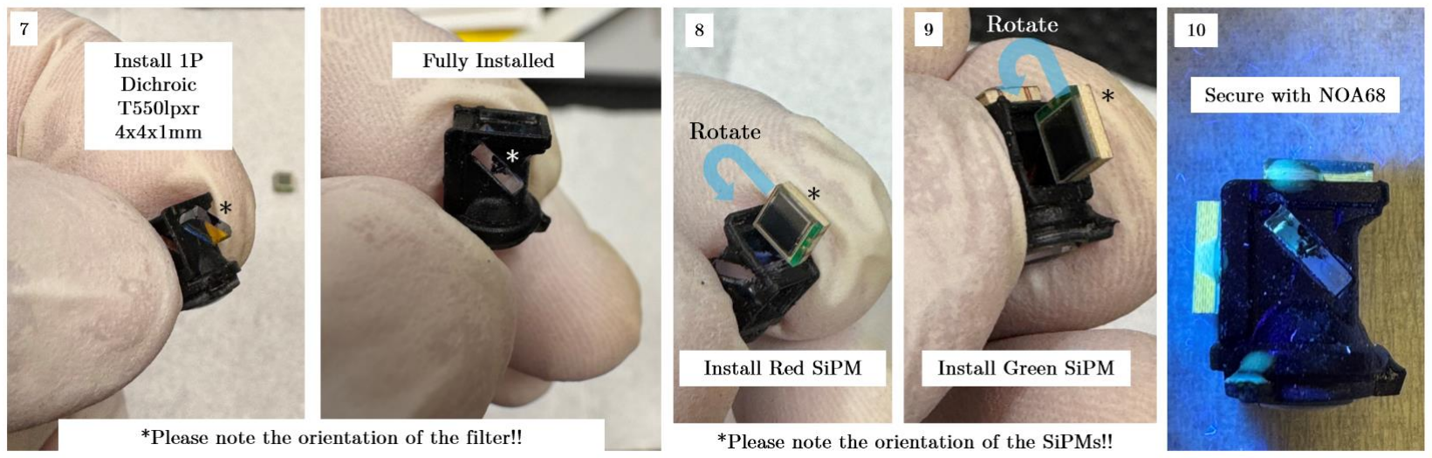
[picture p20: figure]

4. Main Housing Assembly
These components are required for the Main Housing Assembly. Please make sure everything is sourced before beginning.
Component | Part Number | Manufacturer | Unit | Price | Subtotal | Link
Main Housing | Main_Housing.STL | Custom | 1 | $1.00 | $1.00 | Main Housing (https://github.com/golshanilab/UCLA_2P_Miniscope/blob/main/Mechanical%20Designs/STLs%20to%203D%20Print/Main_Housing.STL)
Lens Cover | Lens_Cover.STL | Custom | 1 | $1.00 | $1.00 | Lens Cover (https://github.com/golshanilab/UCLA_2P_Miniscope/blob/main/Mechanical%20Designs/STLs%20to%203D%20Print/Lens_Cover.STL)
Flex-PCB | FLEX-PCB | Custom | 1 | $600.00 | $600.00 | Flex-PCB (https://github.com/golshanilab/UCLA_2P_Miniscope/tree/main/Electronic%20Designs/UCLA%202P%20Miniscope%20FLEX-PCB)
Scan Lens | AC050-010-B | ThorLabs | 2 | $51.38 | $102.76 | Scan Lens (https://www.thorlabs.com/thorproduct.cfm?partnumber=AC050-010-B)
Tube Lens* | OT-1 (Custom) | Optics Technology | 1 | $1,100.00 | $1,100.00 | Tube Lens (https://github.com/golshanilab/UCLA_2P_Miniscope/blob/main/ZEMAX%20Optical%20Designs/Excitation_Path_Full_System.zar)
2P Dichroic (Diced) | ZT775sp-2p, 8x8.5x1mm | Chroma | 1 | $540.00 | $540.00 | 2P Dichroic (https://www.chroma.com/products/parts/zt775sp-2p-multiphoton-shortpass-laser-dichroic)
Torx Screws | 96817A704 | McMaster-Carr | 4 | $0.63 | $2.53 | Torx Screws (https://www.mcmaster.com/96817A704/)
Optical Glue | NOA68 | Norland | 1 | $40.70 | $40.70 | Optical Glue (https://www.thorlabs.com/thorproduct.cfm?partnumber=NOA68)
| | | | | $2,387.99
* Tube lens is custom fabricated, please contact pgolshani@mednet.ucla.edu for more information

This assembly is the most involved and requires 13 steps to build. Finally integrating with all the other assemblies takes another 10 steps.
1. Collect the main housing and the scan lens reamer
2. Ream the hole for scan lens 1. This process is to be done quite lightly by hand and is simply to ensure a snug fit between the housing and the scan lens doublet. There are internal stops in the main housing, so be mindful and only clean up the walls leading to the stop. In our experience this did not need to be completed in a highly accurate fashion.
3. Ream the hole for scan lens 2 in the same way as in step 2.

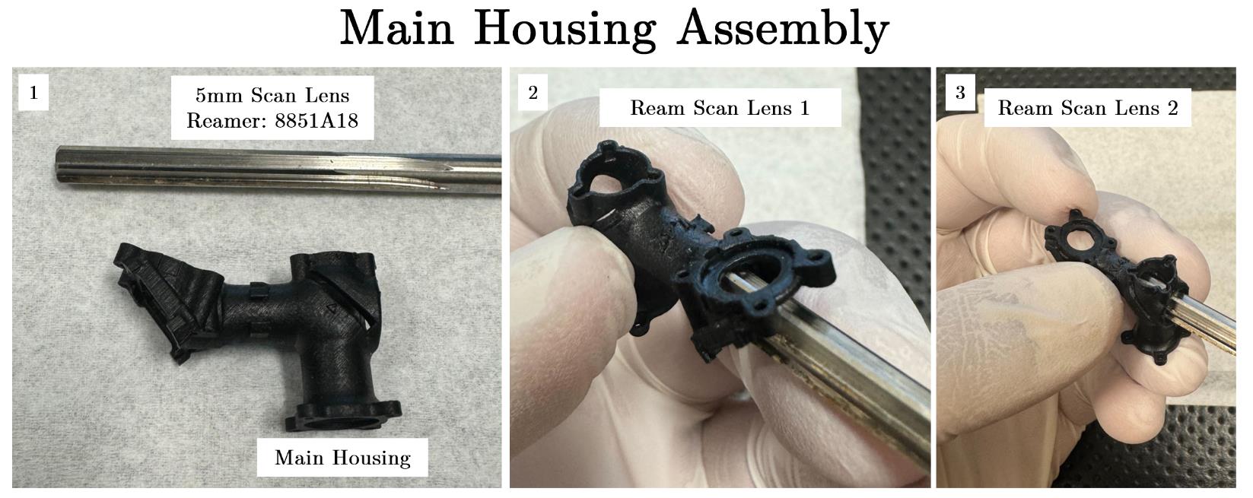
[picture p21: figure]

4. Collect the scan lenses and ensure that the orientation of the lenses is correct. The crown glass for each scan lens should be positioned closest to the scanning mirror.

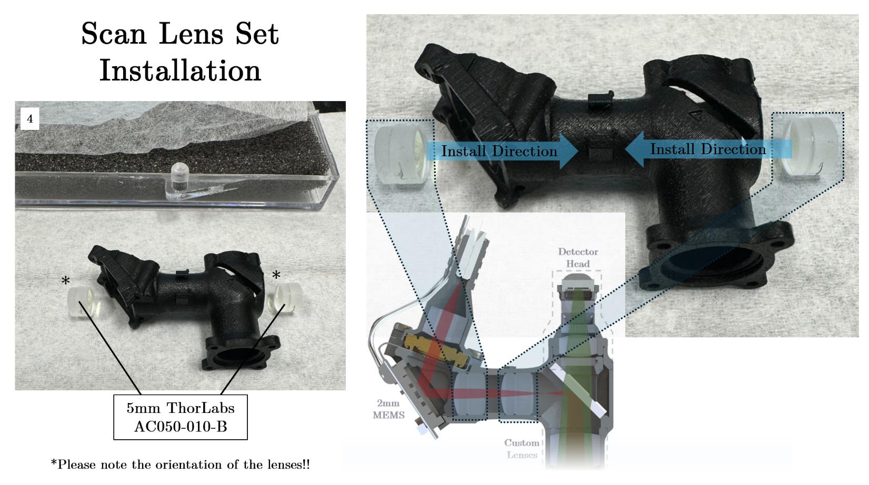
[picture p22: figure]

5. First, we will install scan lens #2, by pushing it through the front of the microscope, opposite the MEMS scanner surface. This can be a little tricky, so take your time and make sure the orientation is maintained. We repeatedly lightly press on opposing edges of the lens to coax it into place.

6. Press the lens into the correct position using a nonabrasive implement. We use dust-free foam swabs from amazon (pictured in the images below) ASIN no. B0CTQCGXP2. Once lens is pressed into place, confirm location with the arrowheads that are fabricated into the microscope housing.

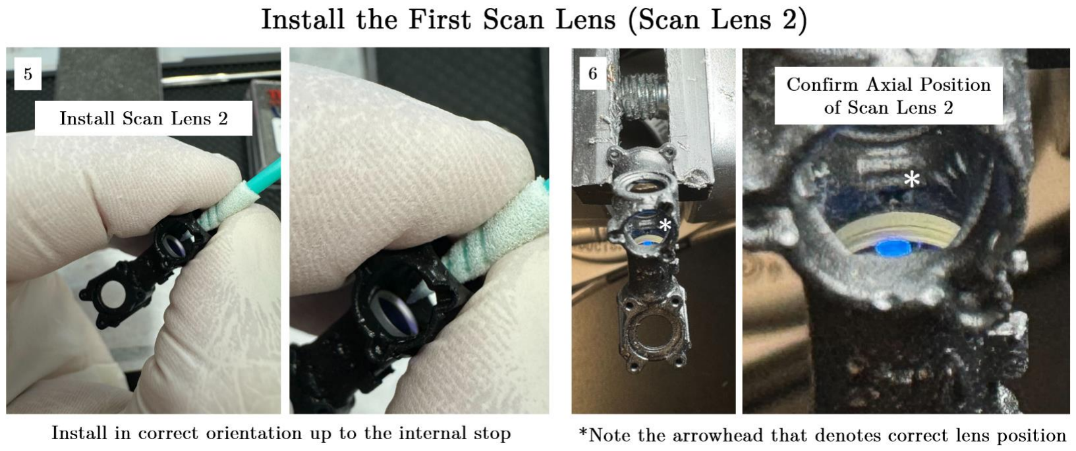
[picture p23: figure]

7. Next, install scan lens #1 from the MEMS scanner side of the microscope using the same technique as in step 5.
8. Confirm placement of scan lens #1 as in step 6.

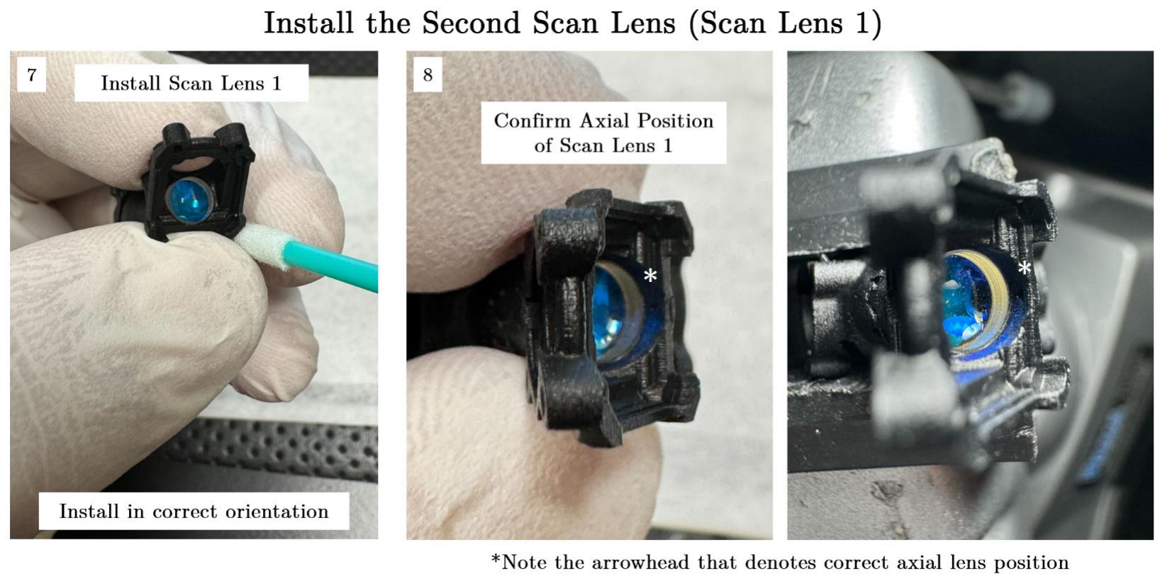
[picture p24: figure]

9. Prepare the tube lens and ensure the orientation in consistent with the figure below. The crown glass is oriented towards the objective.

10. Press the OT tube lens into place following steps 5 and 7 and check the axial position of the doublet as is done in steps 6 and 8. This time the arrowhead is more easily photographed for demonstration purposes.

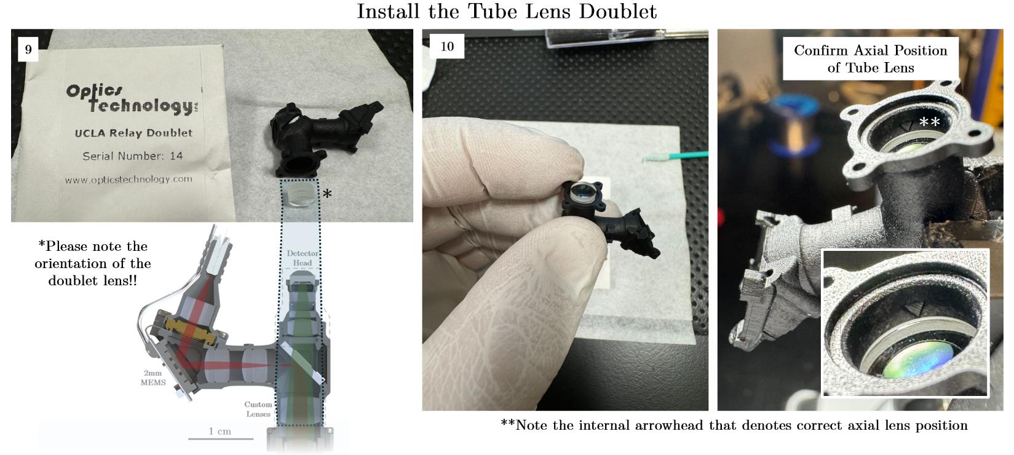
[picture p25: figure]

11. Install the 2P dichroic mirror taking note of the arrow placed on the component by the manufacturer. Make sure it is going through both ends of the slot.
12. Orient the Flex-PCB such that the scanning mirror is pressed up to the mounting surface present in the Main Housing. Ensure there is solid contact without gaps on any end between the LCC package of the scanner and the housing.

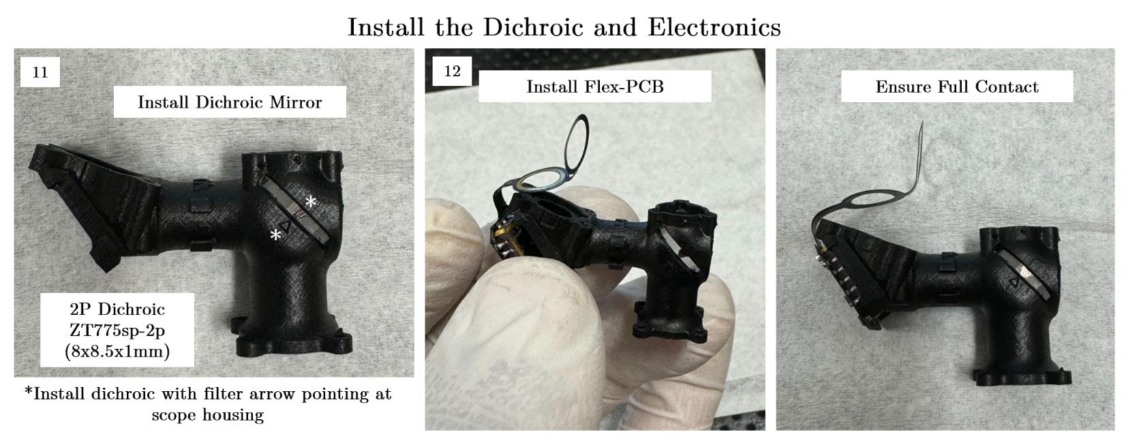
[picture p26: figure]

13. Use NOA68 to fix the MEMS scanner to the main housing. We have had success fixing the sides and bottom surfaces.

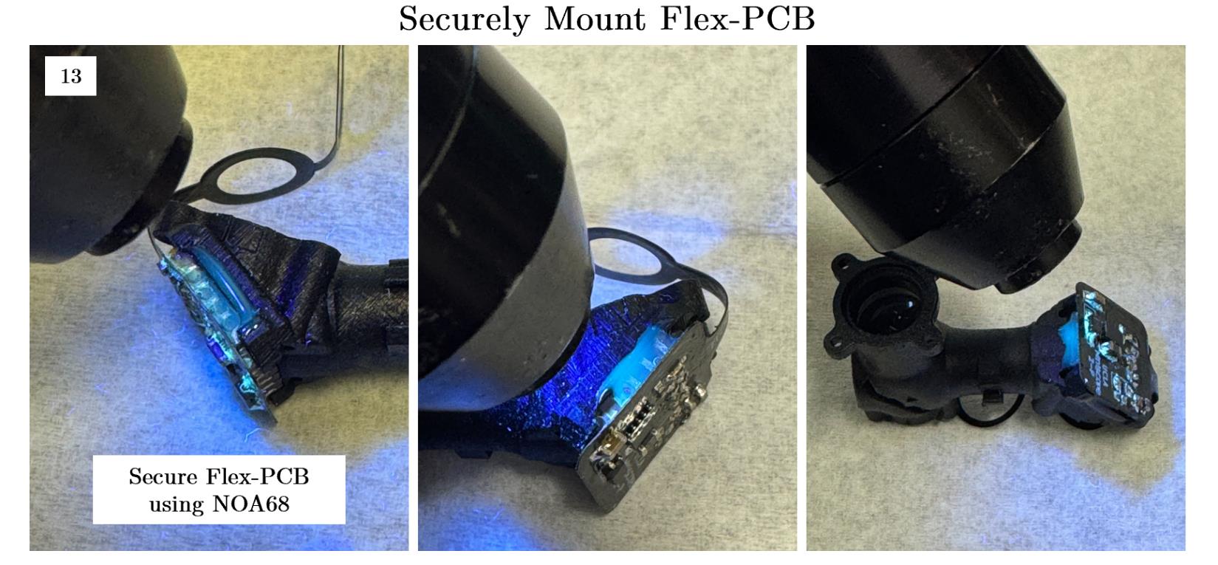
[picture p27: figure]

14. Once the Flex-PCB is secured in place the electrodes for the ETL can be positioned in the following configuration. The main housing has built-in features that are designed to grip the ETL electrodes to hopefully make assembly a bit easier.
15. Next, install the ETL by first placing it on the electrode in the correct orientation described in the figure below.
16. The collimator now needs to be prepared to join the assembly. For this guide, we are demonstrating this assembly without the installed optical fiber. In reality this union of two parts needs to be done after the collimation was defined in the initial part of the assembly guide. This adds a slight complication but the overall technical process is the same.

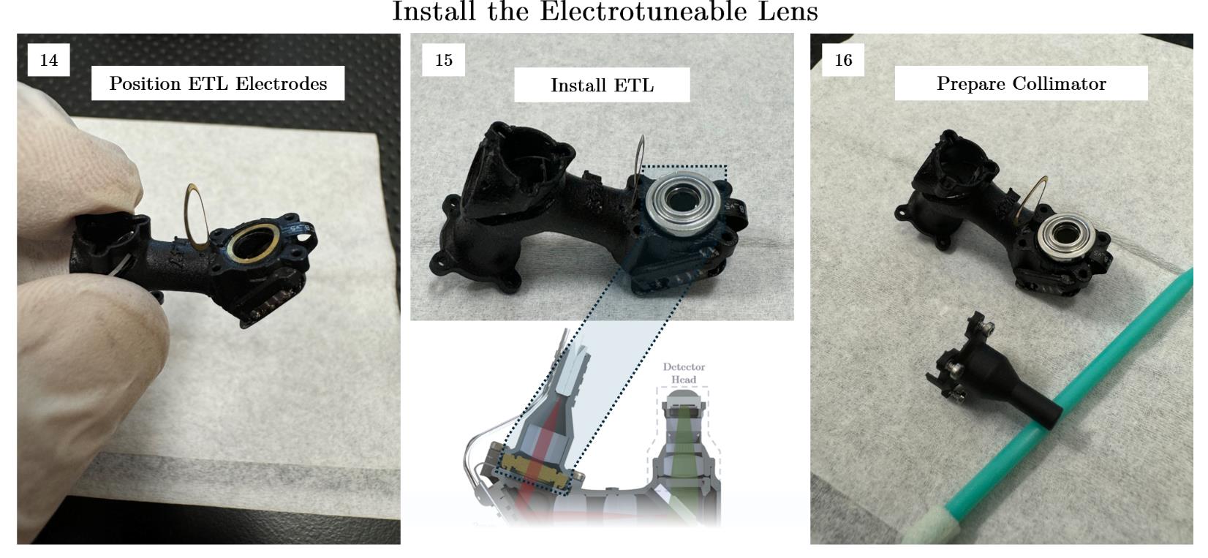
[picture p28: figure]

17. The next step is to join the collimator and main housings. The way this is accomplished most successfully in our experience is to first fit the exposed remaining electrode into the collimator using tweezers, making sure to not scratch the asphere. We then can sandwich the ETL between the collimator and housing, making sure the electrodes are in the correct locations. Since the screws are already in place, we just need to use the torx driver to join the two assemblies. We suggest iteratively tightening screws in a sequential way to avoid excessive torque on any one screw. So lightly tighten all the screws first, then screw them all slightly tighter, until you have solid mechanical contact between the collimator and housing.

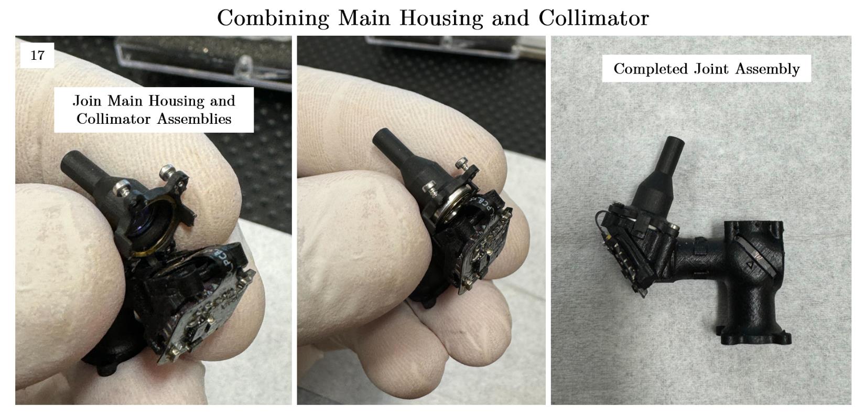
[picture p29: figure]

18. Now the emission filter support can be mounted in place. There is a specific orientation that works best, which involves the long legs of the support resting on the 2P dichroic. Take a look at the mechanical drawings in the manuscript for more information.
19. Next, install the main detector housing by pressing it into place. The housing should be a snug fit but uniformly bottomed-out against the main housing.
20. Add two or three small applications of NOA68 to mechanically mate the detector and main housing. If correctly assembled, this is mainly for peace of mind rather than a required mechanical connection.

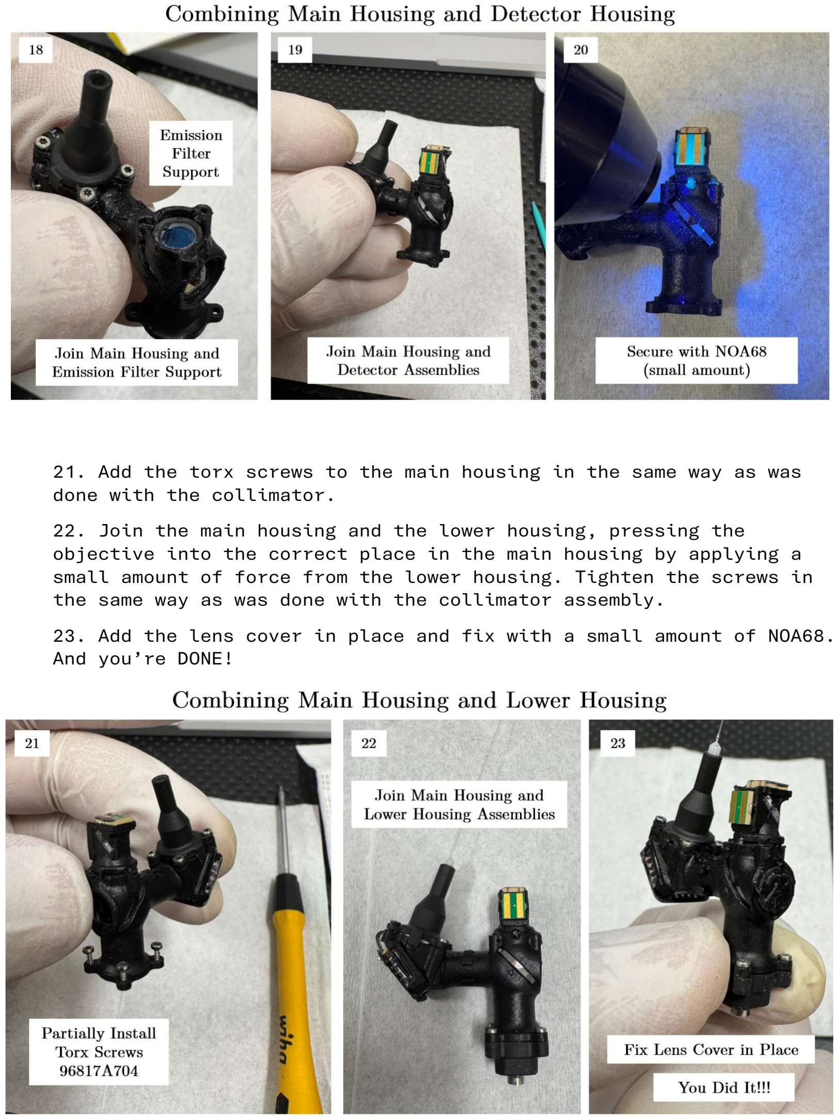
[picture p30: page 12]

21. Add the torx screws to the main housing in the same way as was done with the collimator.
22. Join the main housing and the lower housing, pressing the objective into the correct place in the main housing by applying a small amount of force from the lower housing. Tighten the screws in the same way as was done with the collimator assembly.
23. Add the lens cover in place and fix with a small amount of NOA68. And you’re DONE!

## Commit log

2024-03-28 Main Upload
    20240328
    [2P_Miniscope_FLEX_v3-B_Cu.gbr, 2P_Miniscope_FLEX_v3-B_Mask.gbr, 2P_Miniscope_FLEX_v3-B_Paste.gbr, 2P_Miniscope_FLEX_v3-B_Silkscreen.gbr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]
2025-05-19 Preprocess Filtering
    We've added some resources for filtering a small-amplitude artifact that can be present in some very low-light conditions. In parallel, we have upcoming wiring changes to eliminate this issue altoget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
